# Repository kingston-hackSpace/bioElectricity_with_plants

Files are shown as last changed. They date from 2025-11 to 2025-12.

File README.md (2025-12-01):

# bioElectricity_with_plants (Work-In-Progress)

In this tutorial, we will attempt to monitor the internal electrical activity in a plant. 
The accuracy of the findings, and forms of data visualization are still in work-in-progress. 

Plants naturally move ions (charged particles) through their tissues, and this creates small voltage changes across their cell membranes. These signals tend to shift gradually over time, producing slow drifts with the occasional spike. In this tutorial, our aim is to sense and observe this naturally occurring electrical activity.

***note:** Plant electrical signals are “slow”, meaning they usually change over the course of seconds or minutes rather than instantly.*

***note:** Some plants are more challenging to measure than others. Leaves that are thick, waxy, shiny, very smooth, or very hairy may reduce conductivity or make it difficult for electrodes to adhere properly. Plants with softer, matte, slightly moist, or gently textured leaves—such as pothos, peace lilies, or philodendrons—tend to provide better contact.*

***note:** Environmental electrical noise (from mains power, static, nearby electronics, or loose wires) can affect the readings. More information is provided below.*

---

AMPLIFING PLANT ELECTRICAL SIGNALS
- 

Plant electrical activity is small and subtle, usually in the microvolt (µV) to low-millivolt (mV) range. To sense and observe it, we need a voltage-amplifying device that also performs analogue-to-digital conversion (ADC). In other words, this device boosts the plant’s tiny signals and converts them into numerical values that the Arduino can read.

For this experiment, we will use the HX711 Load-Cell Amplifier.  

HX711 LOAD-CELL AMPLIFIER
-

The HX711 load-cell amplifier is an cheap, high-resolution 24-bit ADC with selectable gain. It is designed to measure very small millivolt-level signals using high-gain differential amplification. Although it was not created specifically for biological measurements, it is a practical choice for this experiment because it offers high sensitivity and is easy to interface with an Arduino. Its sensitivity, however, also means it can easily pick up external electrical noise, which may interfere with the plant readings. Furtheer in this tutorial, we will learn how to reduce environmental electrical noise. 

HOW IT WORKS:
- The HX711 has two input terminals: A+ and A-. The chip measures the voltage difference between these two points (a differential input).

- It supports different gain levels: ×32, ×64, and ×128, allowing it to amplify very small signals.

ELECTRICAL NOISE
-

Our surroundings are full of electrical activity. Mains wiring, chargers, electronic devices, fluorescent lights, Wi-Fi routers, and even our own bodies all generate electric fields. An electric field is simply the region around a charged object where it can influence other charges.

Because the HX711 is designed to detect extremely small voltages, it cannot easily tell the difference between the plant’s bio-electrical signals and electrical noise from the environment. As a result, some noise will inevitably appear in our readings.

In this project, we try to reduce unwanted noise through both hardware and software. However, completely eliminating environmental interference is very difficult, and in practice we aim for readings that are representative rather than perfectly “pure” plant signals.

REDUCING NOISE: TIPS
-

- Use a power-bank to power your Arduino Board. Once you upload the code to the Arduino Board, avoid keeping the board connected to the computer, as it will add electrical interference to your sensings. To visualize the incoming data without a computer, we will send the data from the Arduino to an Android Smartphone via Bluetooth.

- Use short wires whenever possible, as longer wires can act like antennas and pick up environmental electrical noise.

- Use shielded wires for signal connections to further reduce interference.

- Our HX777 Load-Cell amplifier requires two input terminals (A+ and A-). Connect A+ to any leaf, while A- should be connected to the plant's soil (reference point). Grounding our connections will reduce environmental noise from the surrounding electrical fields, as the soil acts as a large conductive plane.
    *Note: You could connect A- to another leaf, but you may capture higher environmental noise.*

- Moistured soil (not dumped) improves conductivity.

- 

SETTING UP BEFORE STARTING
- 
Follow these tutorials **before** trying moving towards the plant project. They will guide you set up everything you need before setting up our plant-project. Complete them in the order provided:

 1. [RGB LED (common anode)](https://github.com/kingston-hackSpace/RGB_LED) 
 2. [HC06 Bluetooth Module](https://github.com/kingston-hackSpace/HC06_Bluetooth_Module) 

-----------------------------------
# TUTORIAL : Monitoring bioElectricity in plants
-----------------------------------
HARDWARE
-
- Arduino UNO
- HX711 Load-Cell Amplifier Module
- HC06 Bluetooth Module
- RGB LED (common anode)
- 220ohms resistor (x3)
- 2.2K resistor
- 1K resistor
- 5V Power Bank
- Android Smartphone
- Electrodes 
  
ELECTRODES
- 
Electrodes are: 

The plant's outer surface (its epidermis or "skin") has cell membranes that hold electrical activity. For this reason, our electrodes can be stick to the plant leaves to sense the electrical activity. Avoid perforating through them, as you can cause them stress. 

TIPS:
- For good contact points use slightly damp connections such as wet-get electrodes.
- You can also make your own electrodes using stainless steel, which has good conductivity, and avoids metal corrossion.
- Don't use copper (corrosive).

WIRING
-

AMPLIFIER 5V --- ARDUINO 5V

AMPLIFIER GND --- ARDUINO GND

AMPLIFIER DATA --- ARDUINO PIN 4

AMPLIFIER CLK --- ARDUINO PIN 5

AMPLIFIER (+) --- PLANT LEAVE

AMPLIFIER (-) --- PLANT SOIL

See wiring reference image [here](https://github.com/kingston-hackSpace/bioElectricity_with_plants/blob/main/Diagram_bb.jpg)

CODE
-

DOWNLOAD Arduino Code [here](https://github.com/kingston-hackSpace/bioElectricity_with_plants/blob/main/ElectricPlant_Test.ino)

Libraries requied: HX711.h

Understanding Data Readings
-
What kind of data do you get when:
- electrodes are lose (no plant connection)
- electrodes are in touch with a human hand
- electrodes are connected to two different leaves
- one electrode is connected to a leave, the other one to the soil
- move the leaves or soil using a wood stick (mechanical stimulation)

FURTHER READING
-

**A) FUTHER READING : TUTORIALS**

PLANTOID PROJECT: http://borsaci06.com/plantoid_project.htm 

**B) FURTHER READING : RESEARCH**

**C) FURTHER READING : MARKET PROJECTS**

PLANT MUSIC :https://www.plantmusic.com.au/about

PLANTS PLAY : https://plantsplay.com/

MUSIC OF THE PLANTS : https://leseli.africa/plantmusic/

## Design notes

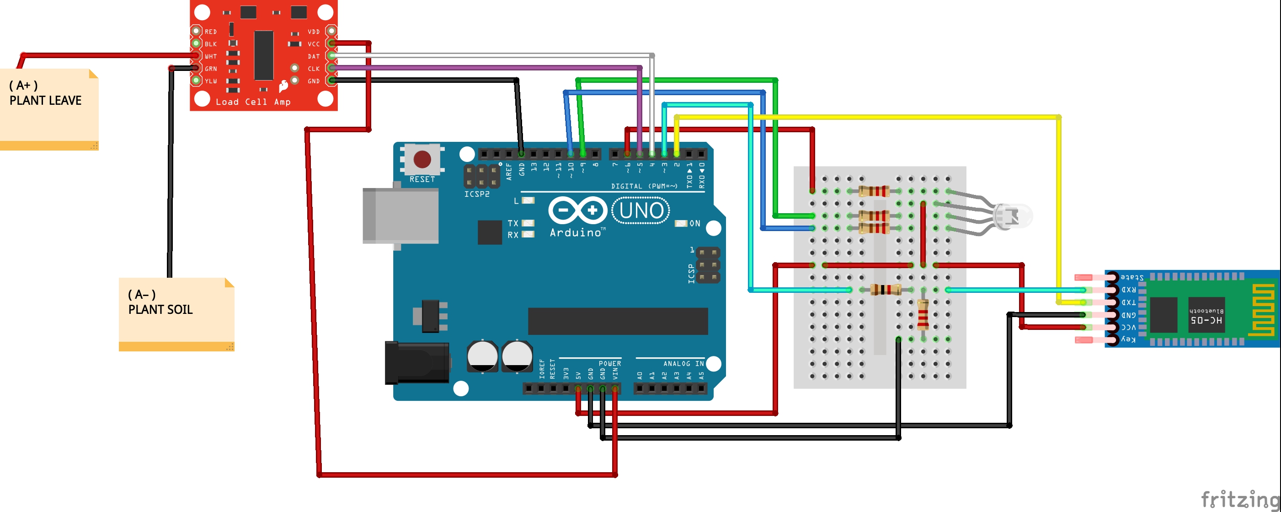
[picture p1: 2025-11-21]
Diagram_bb.jpg

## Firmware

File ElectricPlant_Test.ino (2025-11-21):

#include <SoftwareSerial.h>
#include "HX711.h"

// Pins for HX711
#define HX_DT 4
#define HX_CLK 5

// Pins for RGB LED (common-anode style, 5V connected to LED)
#define RED_PIN 6
#define GREEN_PIN 9
#define BLUE_PIN 10

// Bluetooth
const uint8_t BT_RX = 2;
const uint8_t BT_TX = 3;
SoftwareSerial BTserial(BT_RX, BT_TX);

HX711 scale;

// Smoothing
float filtered = 0.0;
const float filtAlpha = 0.03; // slow smoothing

// Sampling
const unsigned long sampleInterval = 200; // ms
unsigned long lastSample = 0;

// Baseline
long baseline = 0;
const int baselineSamples = 50;

// Spike / noise filter
const int minConsecutive = 3; // number of consecutive readings to trigger change
int consecutiveCount = 0;
long lastStableData = 0;

///////////////////////////////////////////////////
// SETUP
///////////////////////////////////////////////////
void setup() {
  Serial.begin(115200);
  BTserial.begin(9600);

  pinMode(RED_PIN, OUTPUT);
  pinMode(GREEN_PIN, OUTPUT);
  pinMode(BLUE_PIN, OUTPUT);

  digitalWrite(RED_PIN, LOW);
  digitalWrite(GREEN_PIN, LOW);
  digitalWrite(BLUE_PIN, LOW);

  scale.begin(HX_DT, HX_CLK);
  scale.set_gain(128);

  // Compute baseline
  long sum = 0;
  for (int i = 0; i < baselineSamples; i++) {
    while (!scale.is_ready()) delay(1);
    sum += scale.read();
    delay(20);
  }
  baseline = sum / baselineSamples;

  Serial.print("Baseline: ");
  Serial.println(baseline);
  BTserial.println("Bluetooth Communication Successful");
}

///////////////////////////////////////////////////
// LOOP
///////////////////////////////////////////////////
void loop() {
  unsigned long now = millis();
  if (now - lastSample >= sampleInterval) {
    lastSample = now;

    while (!scale.is_ready()) delay(1);
    long raw = scale.read();

    // Adjust relative to baseline
    long adjusted = raw - baseline;

    // Smooth the data
    filtered = filtered * (1 - filtAlpha) + adjusted * filtAlpha;
    long plantData = filtered / 500; // scale down

    // Minimum consecutive filter to avoid random jumps
    if (abs(plantData - lastStableData) > 50) { // arbitrary jump threshold
      consecutiveCount++;
      if (consecutiveCount >= minConsecutive) {
        lastStableData = plantData;
        consecutiveCount = 0;
      }
    } else {
      consecutiveCount = 0;
      lastStableData = plantData;
    }

long greenThreshold = 500; // ±100 is considered green
long minNeg = -3000;       // extreme negative
long maxPos = 3000;        // extreme positive

int r, g, b;  // values before anode inversion

if (plantData < -greenThreshold) {
    // Negative: red → yellow → green
    float t  = float(plantData - minNeg) / float(-greenThreshold - minNeg);
    float tAdj = sqrt(t);   // non-linear mapping

    r = int(255 * (1 - tAdj));  // red strong → fades
    g = int(255 * tAdj);        // green increases
    b = 0;                      // no blue

} else if (plantData > greenThreshold) {

    // Positive: green → cyan → blue
    float t  = float(plantData - greenThreshold) / float(maxPos - greenThreshold);
    float tAdj = sqrt(t);

    r = 0;                       // no red
    g = int(255 * (1 - tAdj));   // green strong → fades
    b = int(255 * tAdj);         // blue increases

} else {
    // Around zero → pure green
    r = 0;
    g = 255;
    b = 0;
}

// Convert to COMMON-ANODE output (invert)
int outR = 255 - r;
int outG = 255 - g;
int outB = 255 - b;

analogWrite(RED_PIN,   outR);
analogWrite(GREEN_PIN, outG);
analogWrite(BLUE_PIN,  outB);

    // Output for monitoring
    Serial.print("Plant Data: ");
    Serial.println(lastStableData);

    BTserial.print("Plant Data: ");
    BTserial.println(lastStableData);
  }
}
